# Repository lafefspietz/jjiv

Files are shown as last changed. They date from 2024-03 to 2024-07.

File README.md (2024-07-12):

# [JJIV](https://github.com/lafefspietz/jjiv/)

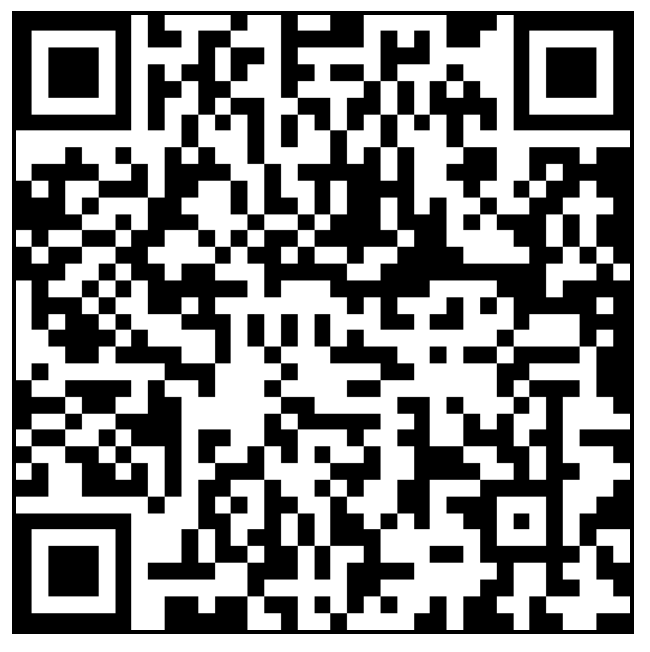
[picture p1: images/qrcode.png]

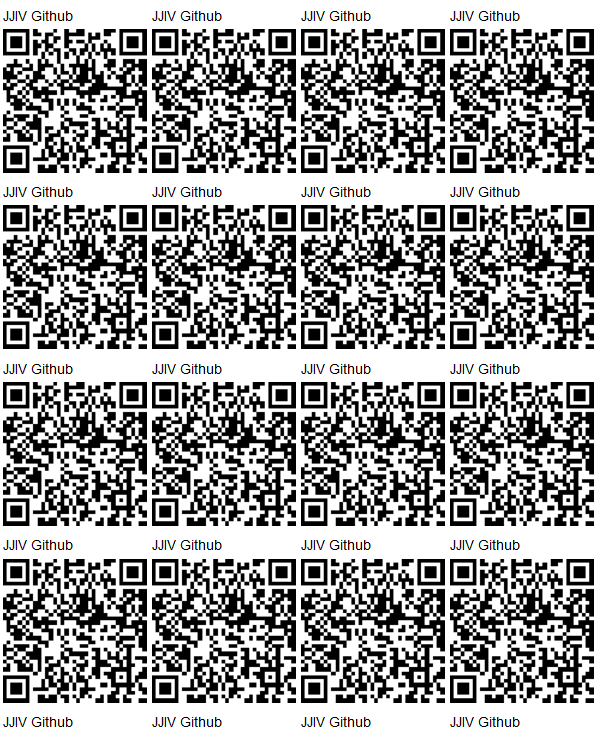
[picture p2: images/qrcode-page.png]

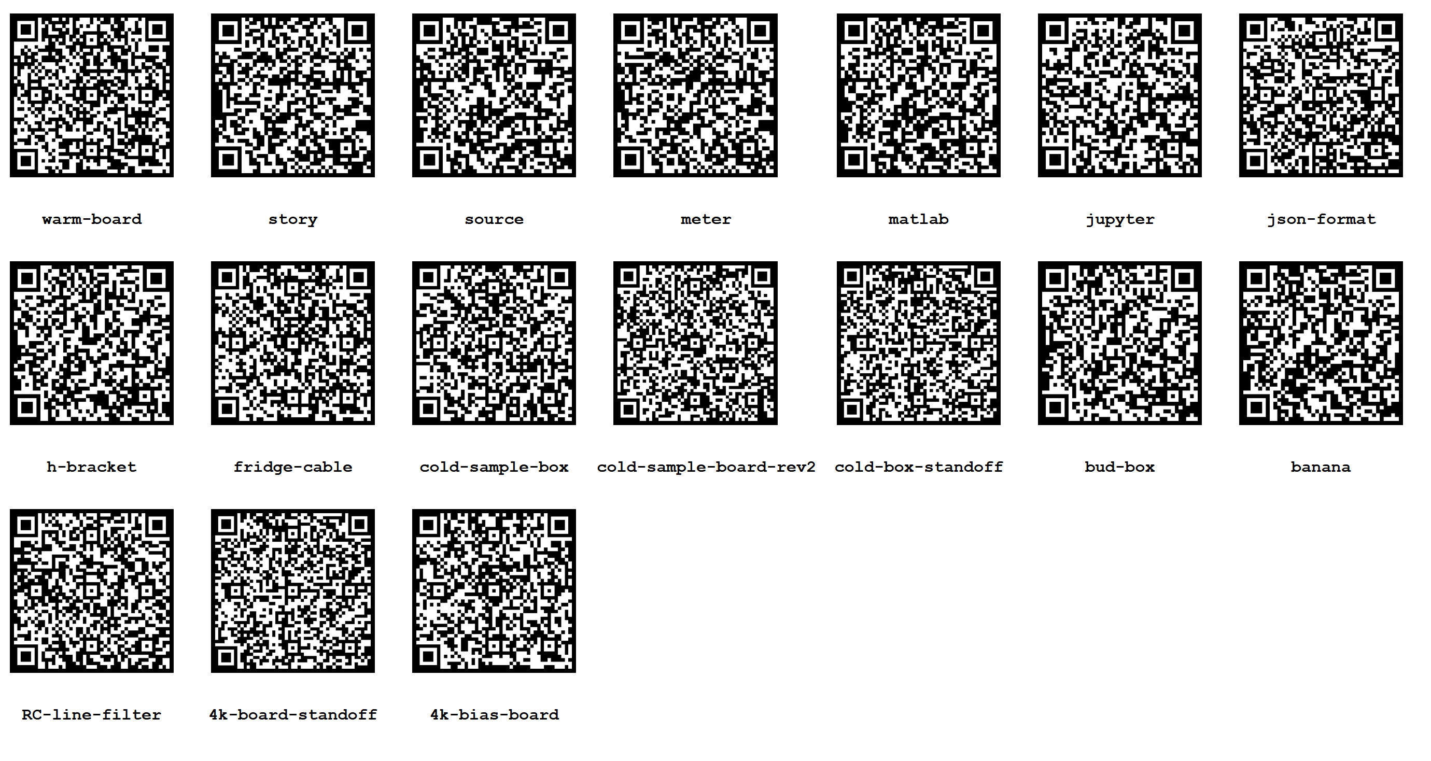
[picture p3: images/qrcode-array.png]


 - [readme reader](readme/readme-reader.html)
 - [readme editor](readme/readme-editor.html)


# JJIV: Josephson Junction IV Curve Tracer System

[Open source hardware instrument](https://github.com/lafelabs/OSHI) for measuring the current-voltage characteristics(IV curves) of [Josephson Junctions](https://en.wikipedia.org/wiki/Josephson_effect) via a true symmetric twisted pair measurement.  

The story behind this system can be read in the [story Readme here](story/README.md).

## Mechanical elements

 - [Bud Box and Rack Mount](bud-box/)
 - [H Bracket](h-bracket/)
 - [4k Board Standoff](4k-board-standoff/)
 - [Sample Enclosure Standoff](cold-box-standoff/)
 - [Sample Enclosure](cold-sample-box/)

## Electrical Elements

 - One [Yokogawa GS200 DC Voltage / Current Source](source/)
 - Two [Volt Meters](meter/)
 - [Banana Cables](banana/)
 - [Warm Board](warm-board/)
 - [DB25 to Fischer Fridge Cable](fridge-cable/)
 - [4k Bias Board](4k-bias-board/)
 - [Sample Board](cold-sample-board-rev2/)
 
## Software Elements

 - [Matlab IV Curves](matlab/)
 - [Data Format](json/)

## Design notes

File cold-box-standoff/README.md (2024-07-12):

## [Back to JJIV](../)

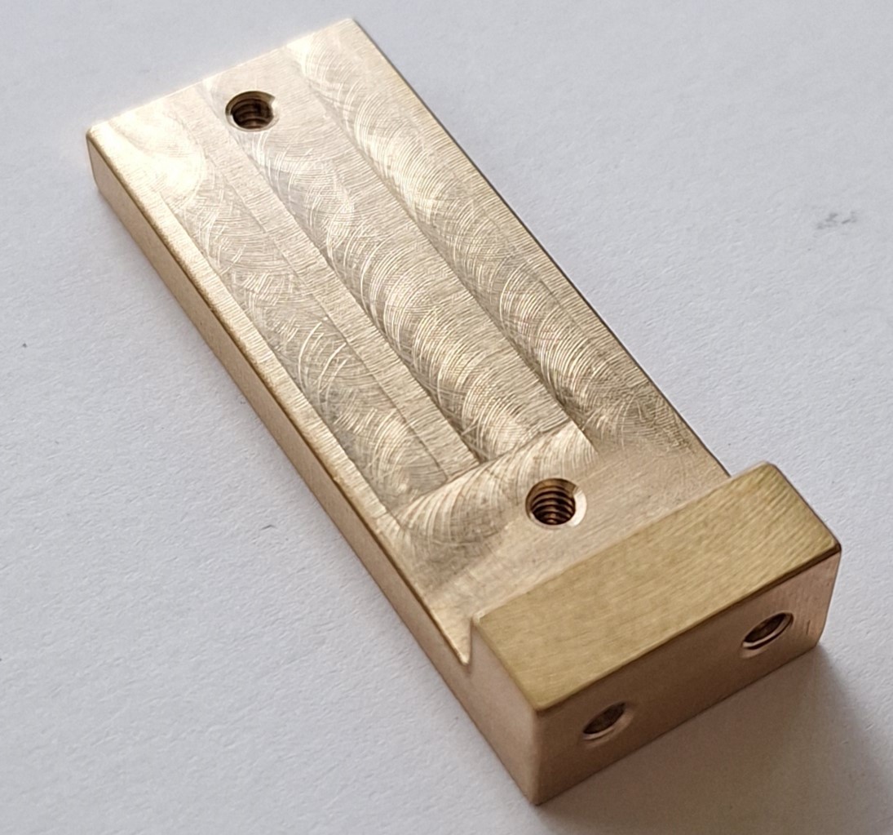
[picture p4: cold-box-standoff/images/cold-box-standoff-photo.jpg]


# Cold Box Standoff

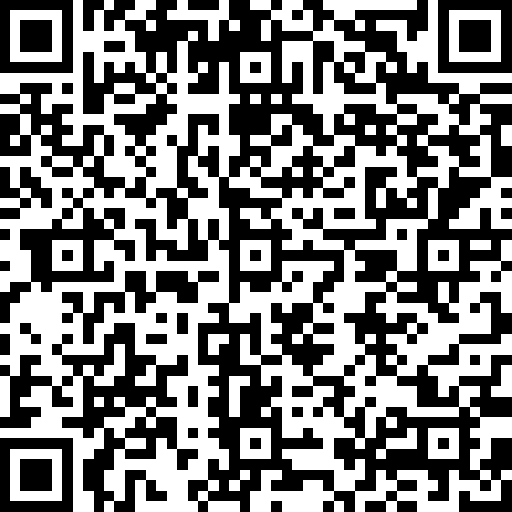
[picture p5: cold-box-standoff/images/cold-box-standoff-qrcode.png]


This brass machined part connects the [H Bracket](../h-bracket/) in the JJIV system with the [cold sample box](../cold-sample-box/) by way of two lenghts of 4-40 brass screws.  In order to order this you will need the .pdf and .step files below.  We had prototypes machined by [pcbway.com](https://pcbway.com) in the spring of 2024.  

These will be made available on artists' web pages so people can buy small numbers of them.

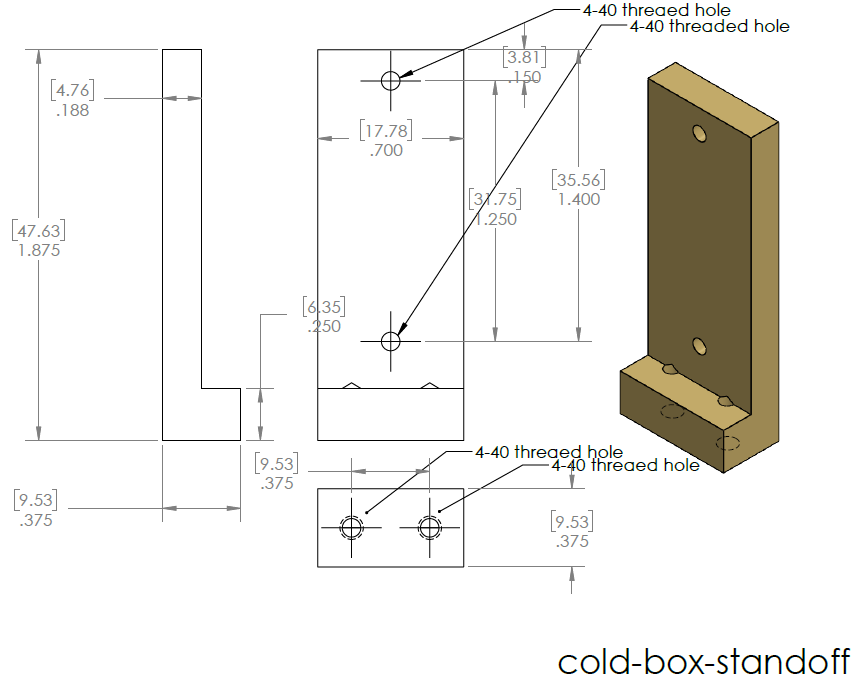
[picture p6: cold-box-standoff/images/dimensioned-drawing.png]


 - [cold-box-standoff.SLDDRW](cold-box-standoff.SLDDRW)
 - [cold-box-standoff.SLDPRT](cold-box-standoff.SLDPRT)
 - [cold-box-standoff.pdf](cold-box-standoff.pdf)
 - [cold-box-standoff.STEP](cold-box-standoff.STEP)
 - [cold-box-standoff.STL](cold-box-standoff.STL)
 
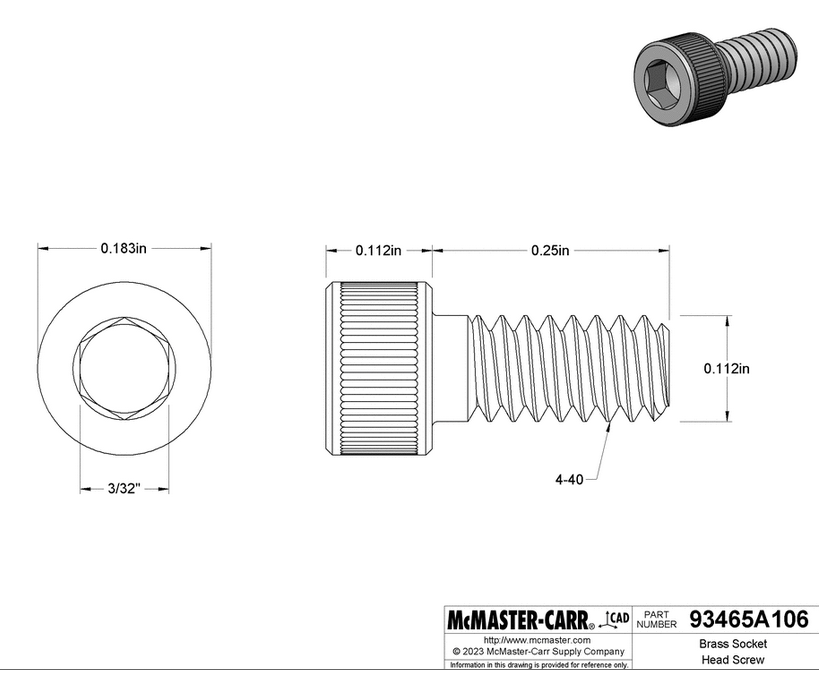
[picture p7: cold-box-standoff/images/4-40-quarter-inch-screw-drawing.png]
(https://www.mcmaster.com/93465A106/)


[Ball-End Hex L-Key, McMaster-Carr part number 57185A11](https://www.mcmaster.com/57185A11/)

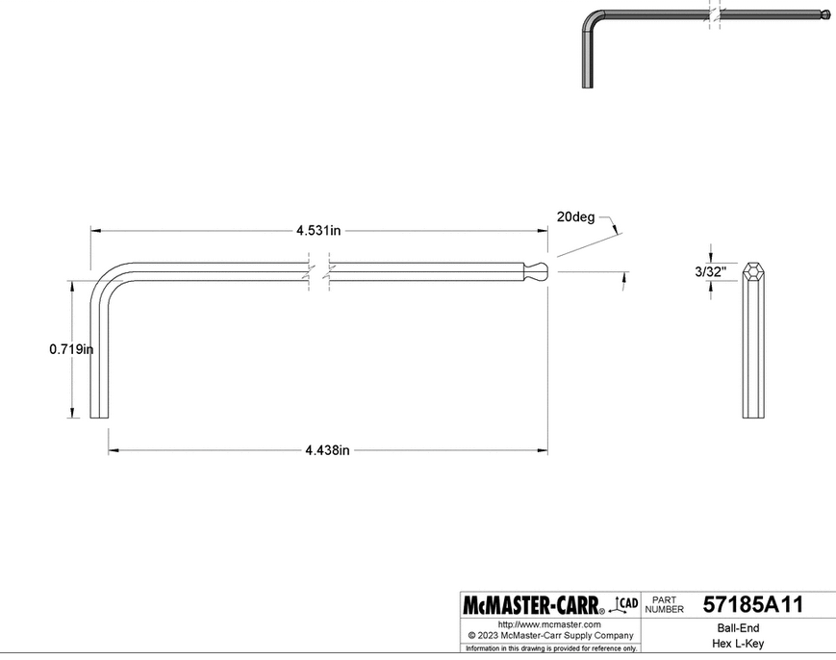
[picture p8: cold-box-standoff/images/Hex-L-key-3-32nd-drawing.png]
(https://www.mcmaster.com/57185A11/)


## T Standoff

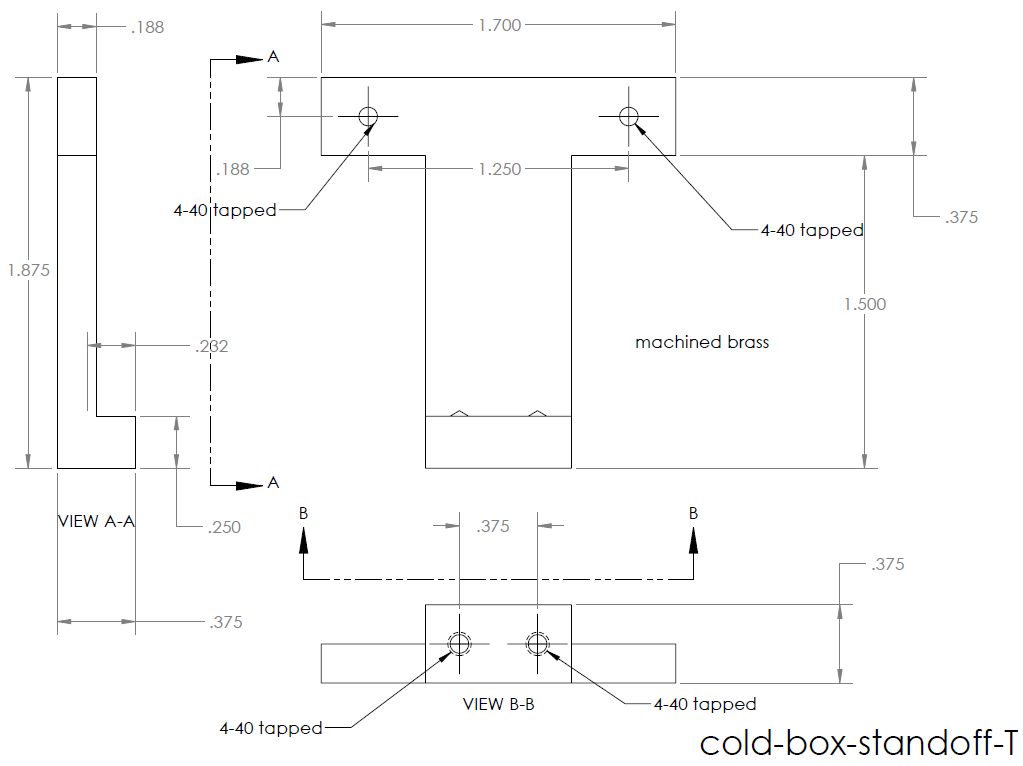
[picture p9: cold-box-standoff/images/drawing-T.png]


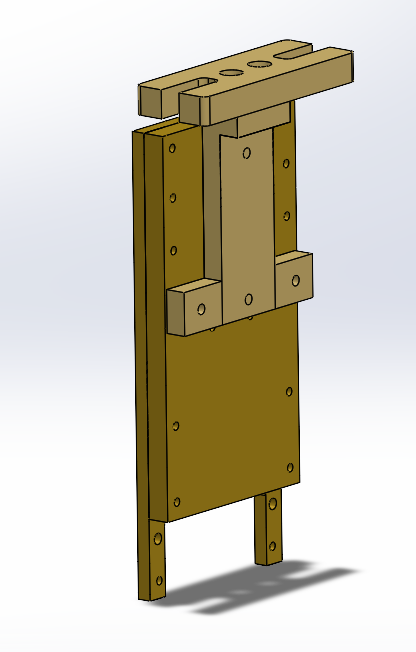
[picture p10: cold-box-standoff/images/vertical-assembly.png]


 - [cold-box-standoff-T.SLDDRW](cold-box-standoff-T.SLDDRW)
 - [cold-box-standoff-T.SLDPRT](cold-box-standoff-T.SLDPRT)
 - [cold-box-standoff-T.STEP](cold-box-standoff-T.STEP)
 - [cold-box-standoff-T.pdf](cold-box-standoff-T.pdf)

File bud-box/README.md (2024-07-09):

## [Back to Main JJIV](../)

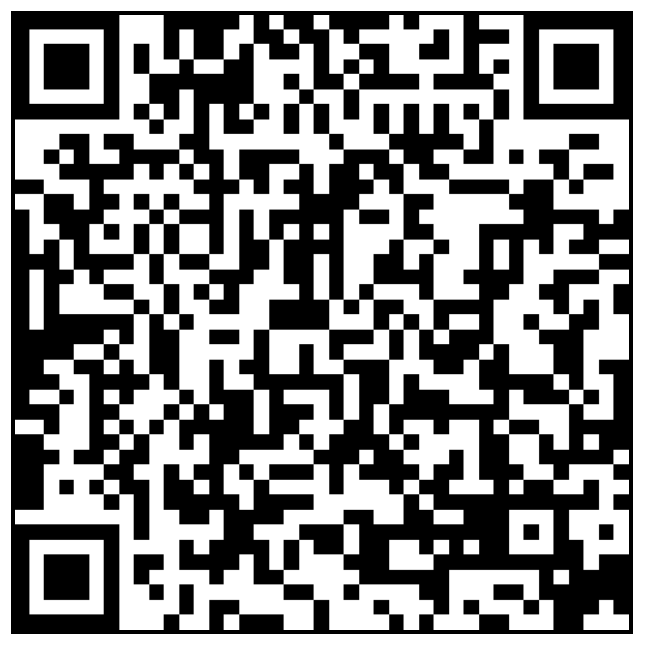
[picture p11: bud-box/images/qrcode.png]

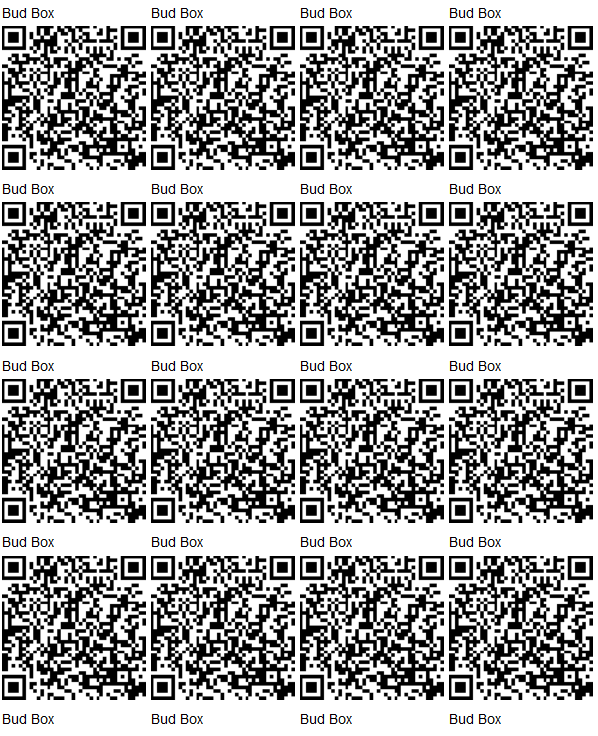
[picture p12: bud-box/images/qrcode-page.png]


# [Bud Box](https://github.com/lafefspietz/jjiv/tree/main/bud-box)

 - [warm Board](../warm-board/)
 - [CU-347 Bud Box from Hawkusa](https://www.hawkusa.com/manufacturers/bud/enclosures/cu-347)
 - [Rack Mount DIN rail from Amazon](https://www.amazon.com/WatchfulEyE-Mounting-Bracket-Aluminum-Oxidation/dp/B08F4WQX1Z)
 - [Din rail clips](https://www.digikey.com/en/products/detail/phoenix-contact/1201578/290934)
 - [Din rail clip screws](https://www.amazon.com/uxcell-100pcs-Stainless-Tapping-Screws/dp/B01M0P3EUK)
 - [2 4/40 standoffs](https://www.mcmaster.com/91075A462/)
 - [1 Isolated BNC feedthrough](https://www.digikey.com/en/products/detail/amphenol-rf/112431/1011725)
 - [1 25 pin DSUB board mount/panel connector](https://www.digikey.com/en/products/detail/assmann-wsw-components/A-DF-25-PP-Z/1241794)
 - [18 5 volt relay from digikey](https://www.digikey.com/en/products/detail/comus-international/3570-1331-053/7497099)
 - [4 position Selector Switch](https://www.digikey.com/en/products/detail/c-k/A10405RNZQ/3751696) 
 - [6 Banana Jacks](https://www.digikey.com/en/products/detail/cinch-connectivity-solutions-johnson/108-0907-001/5932)
 - [6 Banana plug wires](https://www.digikey.com/en/products/detail/pomona-electronics/B-12-4/737916)
 - [3d printed switch knob](knob.stl)
 - [Color coded solid hookup wire](https://www.digikey.com/en/products/detail/adafruit-industries-llc/1311/6198255)

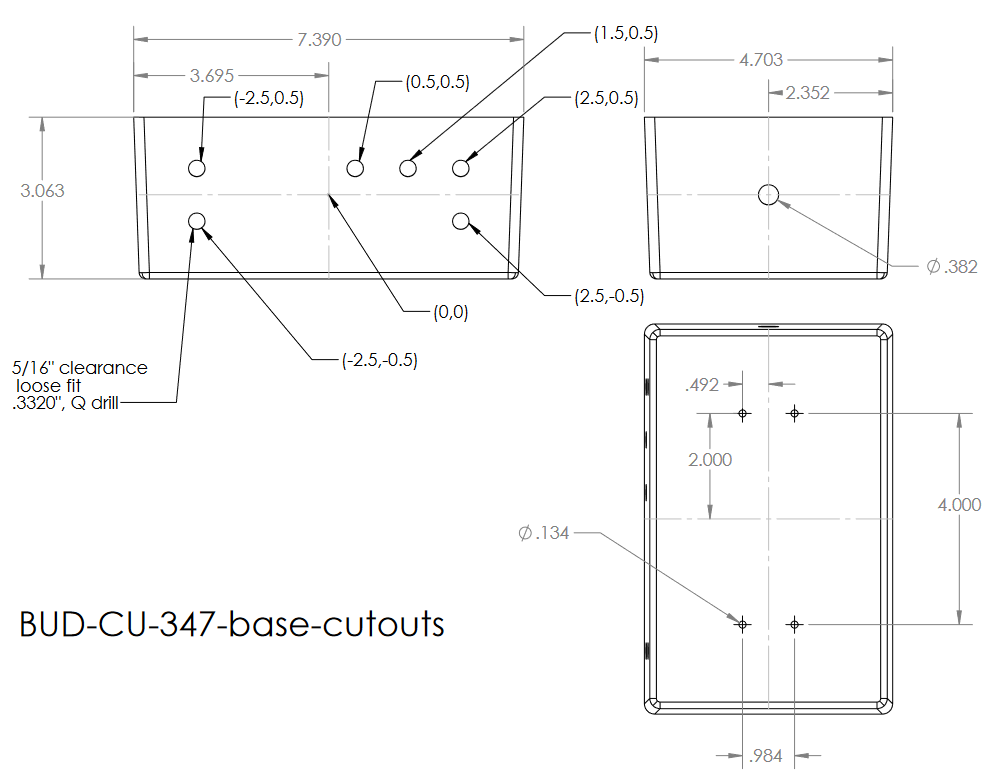
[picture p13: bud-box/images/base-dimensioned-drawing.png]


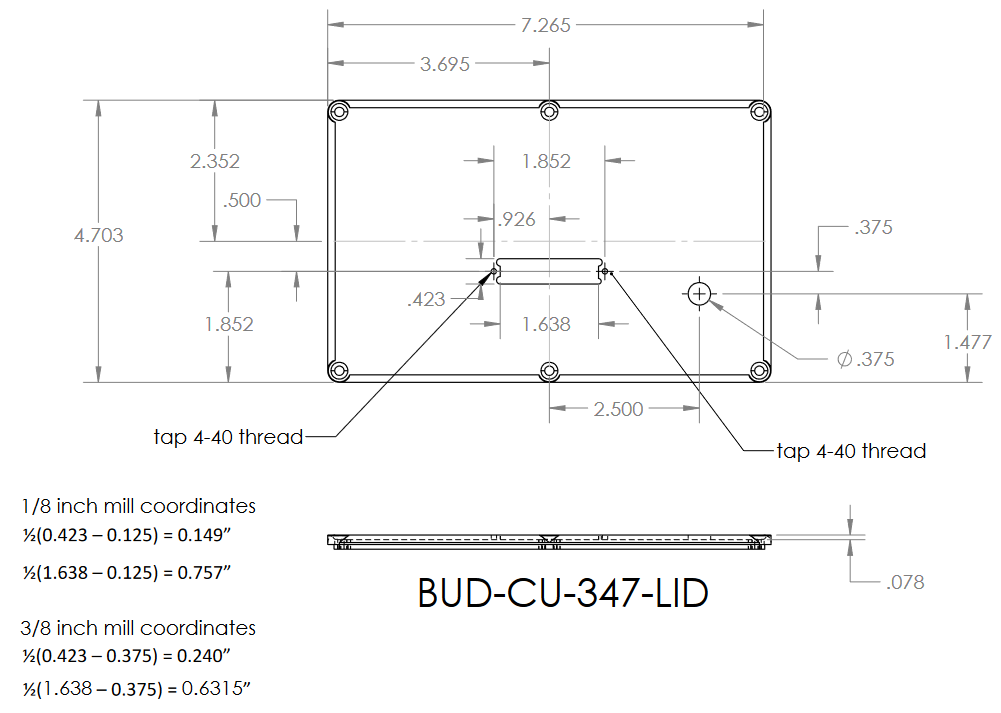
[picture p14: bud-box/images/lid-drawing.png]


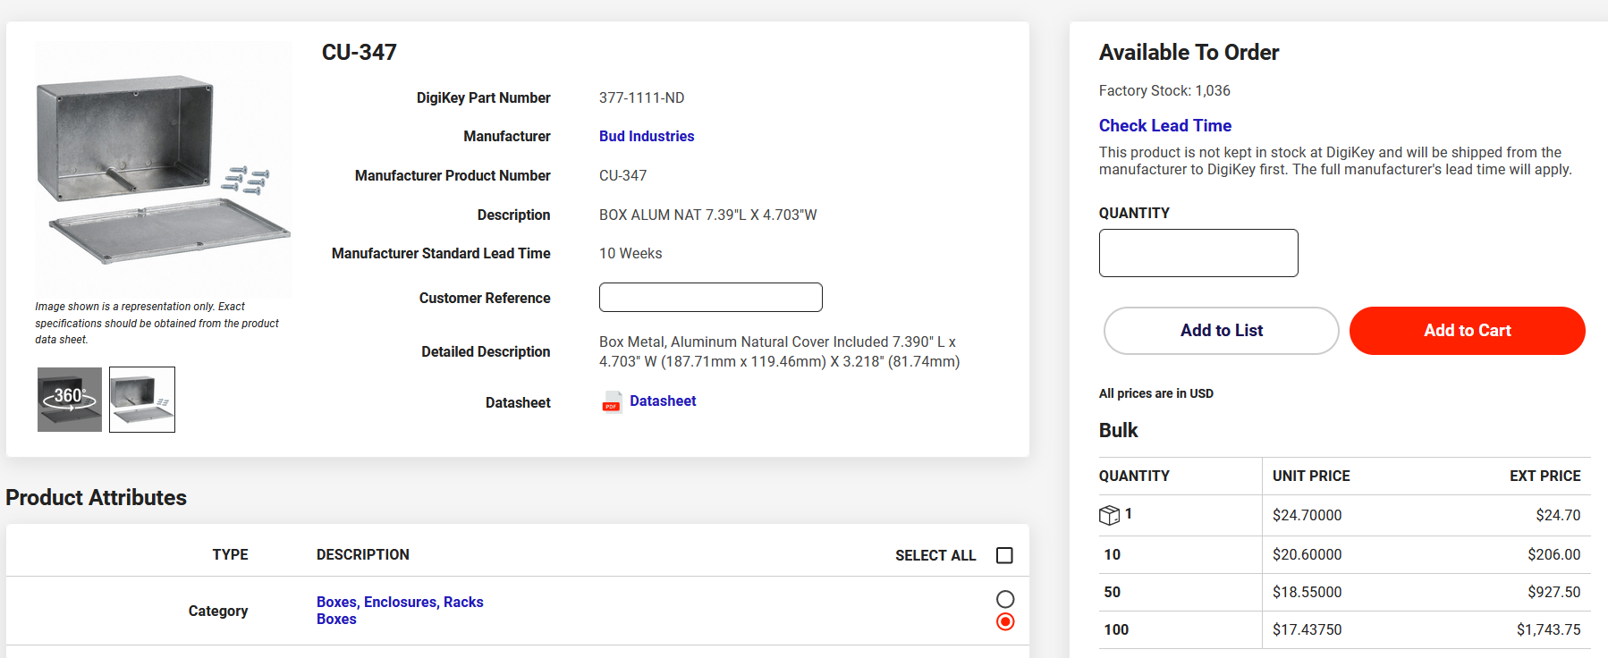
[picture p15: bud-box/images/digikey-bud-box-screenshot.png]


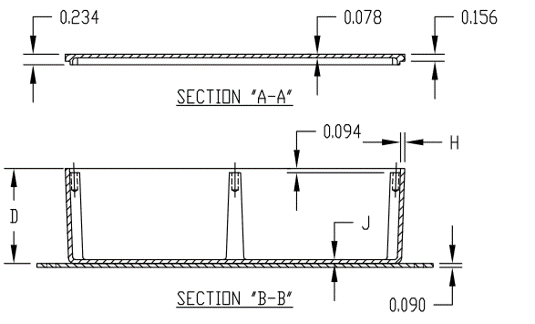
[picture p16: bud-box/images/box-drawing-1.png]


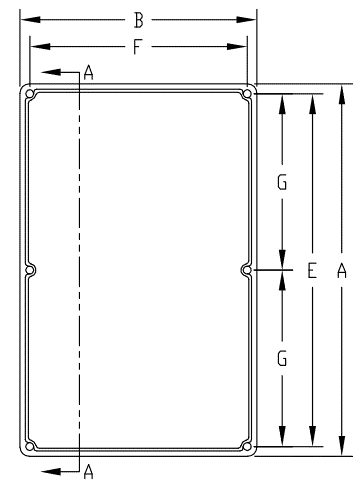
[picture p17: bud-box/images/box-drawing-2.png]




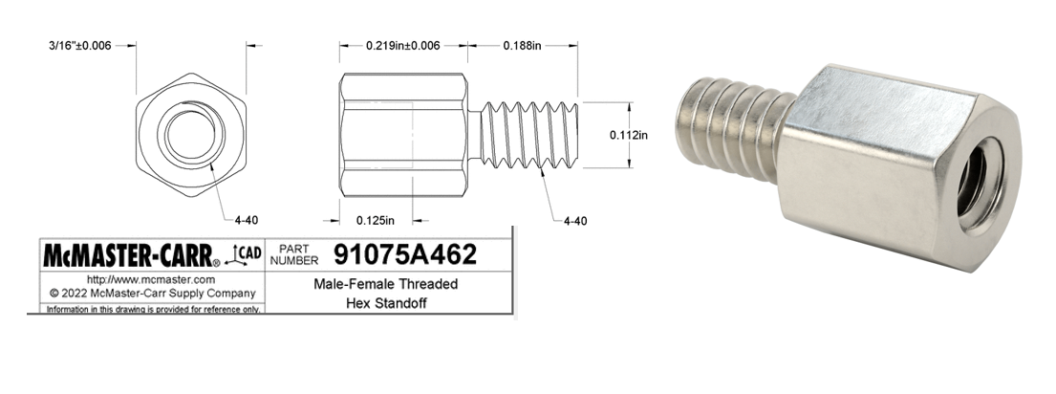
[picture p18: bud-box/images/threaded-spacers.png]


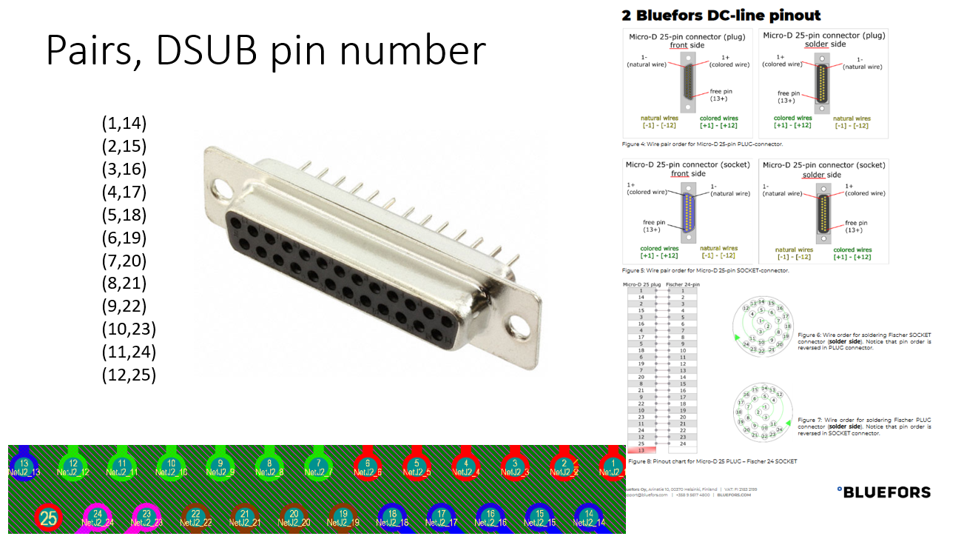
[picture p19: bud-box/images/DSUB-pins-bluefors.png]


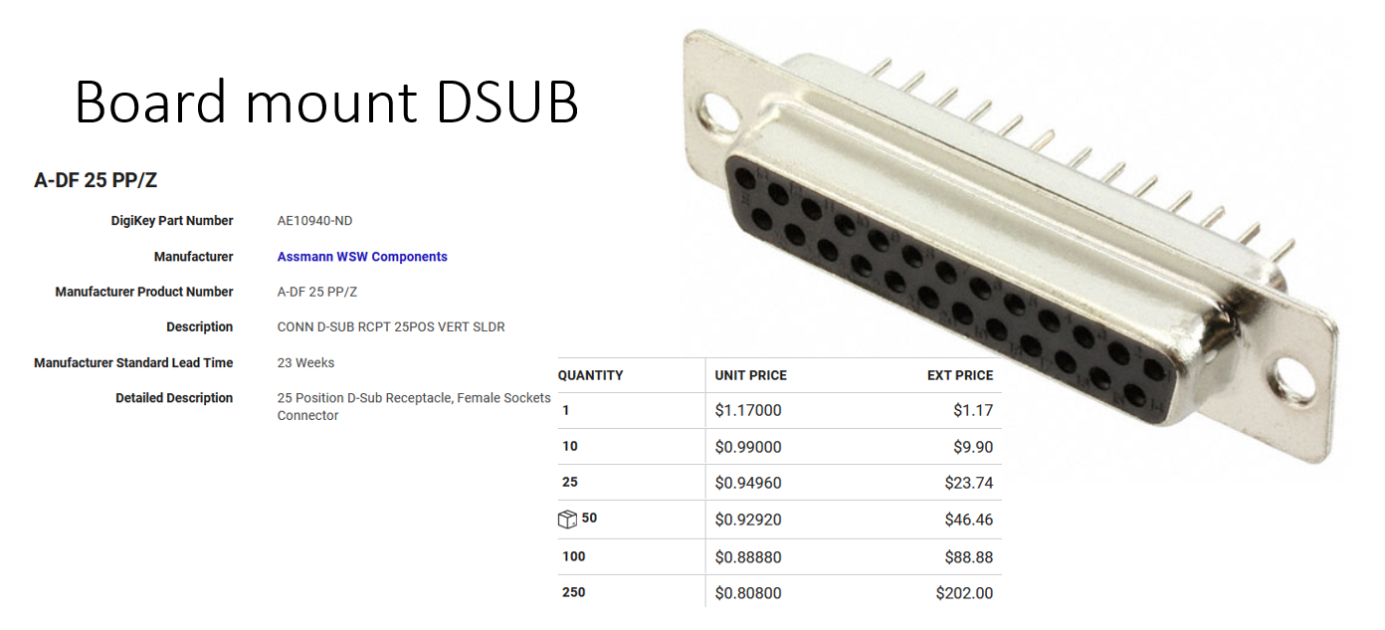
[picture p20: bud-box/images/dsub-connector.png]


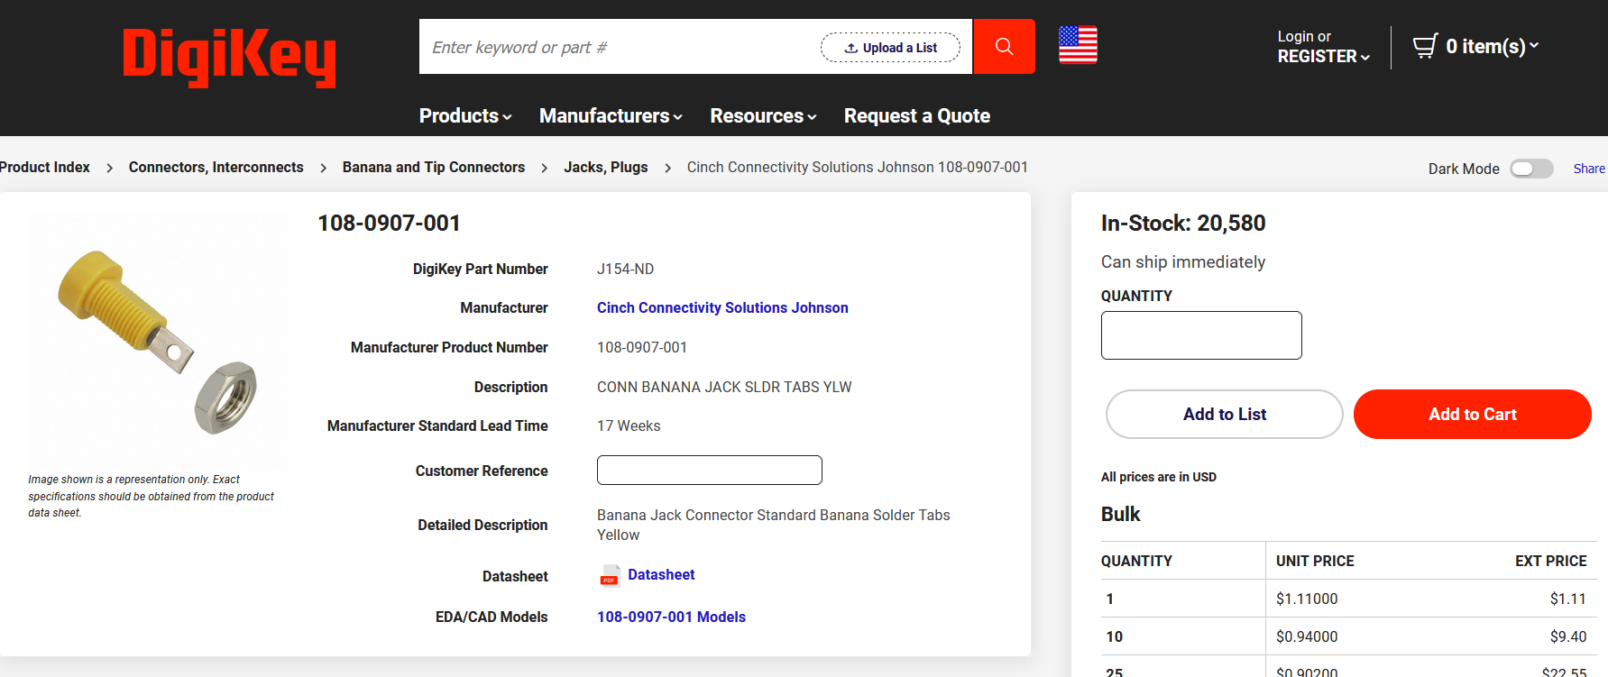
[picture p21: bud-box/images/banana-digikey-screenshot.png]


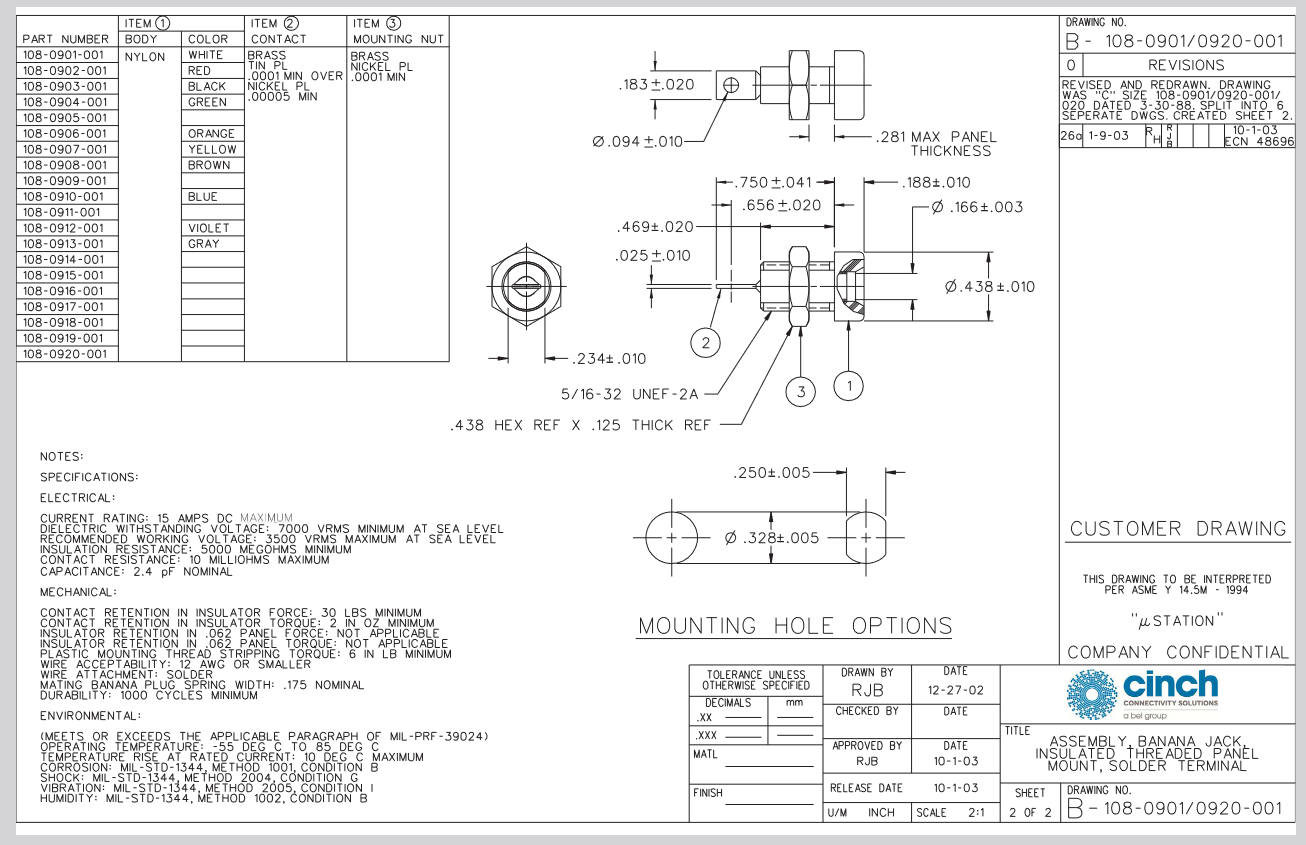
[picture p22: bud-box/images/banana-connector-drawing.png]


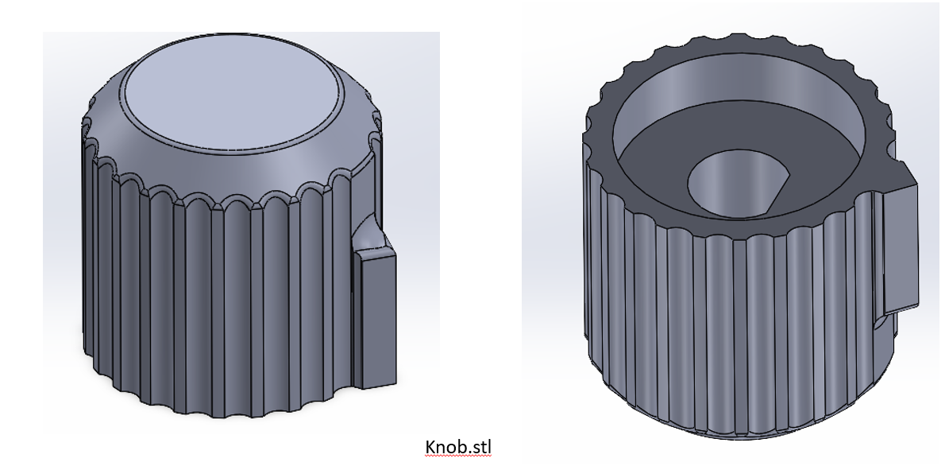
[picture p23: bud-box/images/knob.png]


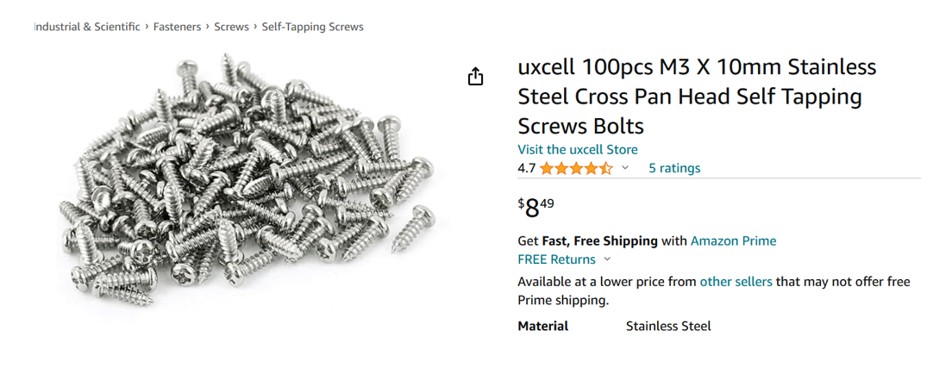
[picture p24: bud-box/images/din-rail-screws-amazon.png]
(https://www.amazon.com/WatchfulEyE-Mounting-Bracket-Aluminum-Oxidation/dp/B08F4WQX1Z)


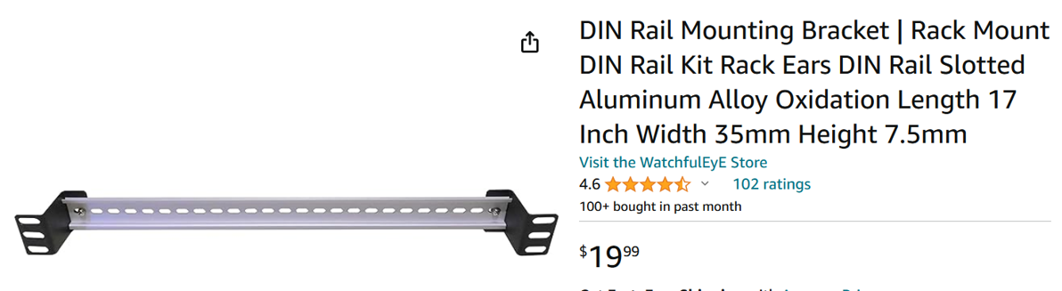
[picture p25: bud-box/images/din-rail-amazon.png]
(https://www.amazon.com/uxcell-100pcs-Stainless-Tapping-Screws/dp/B01M0P3EUK)


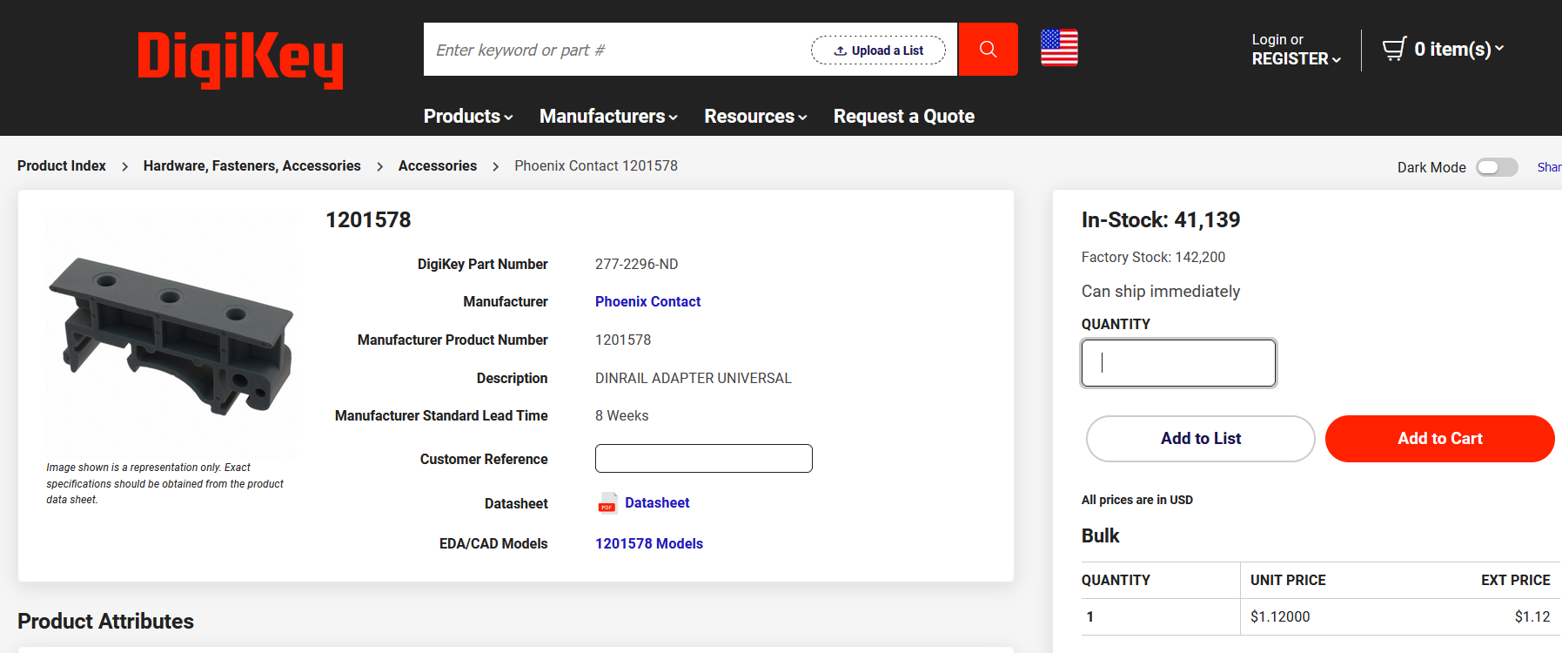
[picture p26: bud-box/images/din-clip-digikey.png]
(https://www.digikey.com/en/products/detail/phoenix-contact/1201578/290934)


## Files

 - [BUD-CU-347-LID.pdf](AN-1304-A-lid-machined.pdf)
 - [BUD-CU-347-LID.SLDPRT](AN-1304-A-machined-box.SLDPRT)
 - [BUD-CU-347-LID.SLDDRW](BUD-CU-347-LID.SLDDRW)
 - [BUD-CU-347-base-cutouts.pdf](BUD-CU-347-base-cutouts.pdf)
 - [BUD-CU-347-base-cutouts.SLDDRW](BUD-CU-347-base-cutouts.SLDDRW)
 - [BUD-CU-347-base-cutouts.SLDPRT](BUD-CU-347-base-cutouts.SLDPRT)
 - [BUD-CU-347-base-cutouts.STEP](BUD-CU-347-base-cutouts.STEP)

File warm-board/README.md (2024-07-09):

## [Back to JJIV](../)

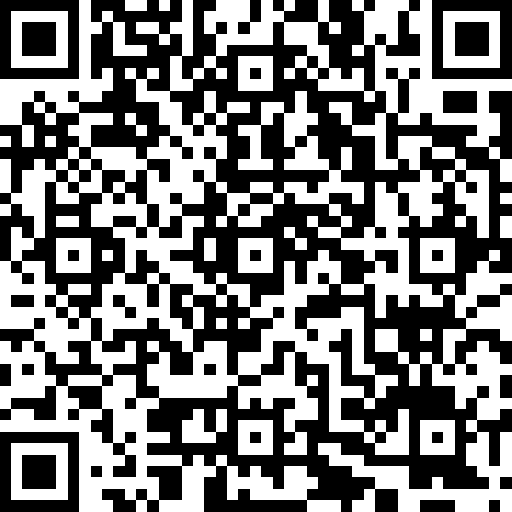
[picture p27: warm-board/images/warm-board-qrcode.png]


# Warm Board



Warm Board is the board that goes inside the [Bud Box](../bud-box) which connects the DB25 connector which goes to the dilution refrigerator with the drive, current leads and voltage leads by way of a network of electromechanical relays.  

## Files

 - [warm-pcb-gerbers.zip](warm-pcb-gerbers.zip)
 - [warm-pcb.step](warm-pcb.step)
 - [warm-board.PrjPcb](warm-board.PrjPcb)
 - [warm-board.SchDoc](warm-board.SchDoc)
 
## Bill of Materials(BOM)

 - [1x DB 25 through hole Board connector](https://www.digikey.com/en/products/detail/assmann-wsw-components/A-DF-25-PP-Z/1241794)
 - [2x 4-40 Standoffs](https://www.mcmaster.com/91075A462/)
 - [18x Relay](https://www.digikey.com/en/products/detail/comus-international/3570-1331-053/7497099)
 - [1x 4 Way Switch](https://www.digikey.com/en/products/detail/c-k/A10405RNZQ/3751696)
 - [Color coded solid hookup wire](https://www.digikey.com/en/products/detail/adafruit-industries-llc/1311/6198255)
 - [6x Banana Jacks](https://www.digikey.com/en/products/detail/cinch-connectivity-solutions-johnson/108-0907-001/5932)
 - [Isolated BNC Feedthrough for power]( https://www.digikey.com/en/products/detail/amphenol-rf/112431/1011725)

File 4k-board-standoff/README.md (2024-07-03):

## [Back to Main JJIV](../)




# [4 kelvin board standoff](https://github.com/lafefspietz/jjiv/tree/main/4k-board-standoff)

This is the machined brass standoff which connects the [H Bracket](../h-bracket/) with the [../4k-bias-board/].  It has 4-40 threaded holes which are used for both of these connections.  To order these from a machine shop you will need the .pdf and .step files below.  



## Files

 - [4k-board-standoff.SLDPRT](4k-board-standoff.SLDPRT)
 - [4k-board-standoff.SLDDRW](4k-board-standoff.SLDDRW)
 - [4k-board-standoff.pdf](4k-board-standoff.pdf)
 - [4k-board-standoff.STEP](HBracket-M4.STEP)
 - [4k-board-standoff.STL](4k-board-standoff.STL)
 - [1/4 inch 4-40 Brass Screw model](93465A106_Brass-Socket-Head-Screw.SLDPRT)







[Quarter inch 4-40 brass socket head screw, McMaster-Carr part number 93465A106](https://www.mcmaster.com/93465A106/)

(https://www.mcmaster.com/93465A106/)

[Ball-End Hex L-Key, McMaster-Carr part number 57185A11](https://www.mcmaster.com/57185A11/)

(https://www.mcmaster.com/57185A11/)

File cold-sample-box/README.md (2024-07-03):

## [Back to JJIV](../)



# Cold Sample Box

This metal box closes directly over the bare copper on the circuit board, and the soldermask covering the lines going into the sample space.  There is about 1 mm vertical distance in the cavity where the samples are placed.  RF absorbent foam can be used over the RC line filters in the [cold sample board](../cold-sample-board-rev2/) to further block very high frequency signals. 

This enclosure aims to be a very cold and dark space with effective heat sinking to the base of a dilution refrigerator.  The two parts are held together with 2-56 screws, and are attached to the [cold box standoff](../cold-box-standoff/) by 4-40 screws.  

We had the prototypes built out of brass by [PCBWay.com](https://pcbway.com) in the spring of 2024, and are testing them now over the summer of 2024.  To order them from any machine shop, you will need the .pdf and the .step files below.  You need to get both a top and a bottom for each JJIV kit.  Also listed below are the screws you need to assemble everything and the hex wrenches for those screws. It's always a good idea to add those hex wrenches to your parts order so you don't have to hunt for those sizes during assembly.

These can be bought and sold by artists on the Internet as well, to take advantage of economies of scale from the machine shop.





 - [cold-sample-box-bottom.pdf](cold-sample-box-bottom.pdf)
 - [cold-sample-box-bottom.STEP](cold-sample-box-bottom.STEP)
 - [cold-sample-box-bottom.SLDPRT](cold-sample-box-bottom.SLDPRT)
 - [cold-sample-box-bottom.SLDDRW](cold-sample-box-bottom.SLDDRW)
 


 - [cold-sample-box-top.pdf](cold-sample-box-top.pdf)
 - [cold-sample-box-top.SLDDRW](cold-sample-box-top.SLDDRW)
 - [cold-sample-box-top.SLDPRT](cold-sample-box-top.SLDPRT)
 - [cold-sample-box-top.STEP](cold-sample-box-top.STEP)
 
## Fasteners

 - [2-56 brass socket cap screws 5/16" length McMAster Part number 93465A078](https://www.mcmaster.com/93465A078/)
 - [4-40 brass socket cap screws 3/8" length McMaster part number 93465A108](https://www.mcmaster.com/93465A108/)
 - [5/64 Allan Wrench](https://www.mcmaster.com/57185A43/)
 - [3/32 Allan Wrench](https://www.mcmaster.com/57185A11/)

(https://www.mcmaster.com/93465A078/)

(https://www.mcmaster.com/93465A108/)

(https://www.mcmaster.com/57185A11/)

(https://www.mcmaster.com/57185A43/)

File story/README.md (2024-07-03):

## [Back to JJIV](../)

# JJIV Story



[Josephson Junctions](https://en.wikipedia.org/wiki/Josephson_effect) are electronic devices consisting of two superconducting electrodes separated by an insulating barrier thin enough to allow for [quantum tunneling](https://en.wikipedia.org/wiki/Quantum_tunnelling).  They are analog devices that have been used for [voltage standards](https://en.wikipedia.org/wiki/Josephson_voltage_standard), mixers, detectors, synthesizers, and as the main element to the [superconducting approaches](https://en.wikipedia.org/wiki/Superconducting_quantum_computing) to [quantum computer](https://en.wikipedia.org/wiki/Quantum_computing) development.

This is a system for measuring current-voltage(IV) curves of low critical current(10's of nanoamps) Josephson junctions in a dilution refrigerator.  This work is being carried out in the Superconductive electronics group in the Radio Frequency Division of the Communications Technology Laboratory at the National Institute of Standards and Technology, in Boulder, Colorado.  

The initial system is built for use on a Bluefors dilution refrigerator using the built in twisted pair wiring that ships with those instruments.  

The system consists of a programmable voltage source, a pair of volt meters, a room temperature box which switches the signals between different samples, a connecting that box to the dilution fridge, a bias board with a cold voltage divider and bias resistors, and a cold sample assembly with built in filtering.      

This documentation is intended to allow other researchers to replicate the entire set of components to make a turnkey system for taking IV curves of low critical current Josephson Junctions at dilution refrigerator temperatures.  



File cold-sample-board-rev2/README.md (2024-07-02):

## [Back to JJIV](../)





# Cold Sample Board rev 2 

 - [cold-sample-board-rev2.PcbDoc](cold-sample-board-rev2.PcbDoc)
 - [cold-sample-board-rev2.pdf](cold-sample-board-rev2.pdf)
 - [cold-sample-board-rev2.PrjPcb](cold-sample-board-rev2.PrjPcb)
 - [cold-sample-board-rev2.SchDoc](cold-sample-board-rev2.SchDoc) 
 - [cold-sample-board-rev2.step](cold-sample-board-rev2.step) 
 - [cold-sample-board-rev2-bom.xlsx](cold-sample-board-rev2-bom.xlsx) 
 - [cold-sample-board-rev2-gerbers.zip](cold-sample-board-rev2-gerbers.zip) 
 - [cold-sample-board-rev2-gerbers.zip](cold-sample-board-rev2-gerbers.zip) 
 - [Pick Place for cold-sample-board-rev2.txt](Pick-Place-for-cold-sample-board-rev2.txt)

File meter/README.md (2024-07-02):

## [Back to JJIV](../)



# Meter



We need two of these to take IV curves, one for the voltage and one for the current. They are controlled via GPIB in [Matlab](../matlab).

 - [keysight link](https://www.keysight.com/us/en/product/34401A/digital-multimeter-6-digit.html)
 - [Used from bellnw for $895](https://www.bellnw.com/products/keysight-34401a)
 - [Used from valuetronics for $795](https://www.valuetronics.com/product/34401a-agilent-multimeter-used)

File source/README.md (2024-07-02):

## [Back to JJIV](../)



# Source

One Yokogawa GS200 voltage source drives the twisted pairs.



 - [yokogawa link](https://tmi.yokogawa.com/us/solutions/products/generators-sources/source-measure-units/gs200/)
 - [Used from transcat for $3,995](https://www.transcat.com/yokogawa-gs210-used-for-sale-dc-voltage-current-source)

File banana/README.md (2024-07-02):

## [Back to JJIV](../)





# Banana

 - [Banana jack](https://www.digikey.com/en/products/detail/cinch-connectivity-solutions-johnson/108-0907-001/5932)
 - [Banana Cable](https://www.digikey.com/en/products/detail/pomona-electronics/B-12-4/737916)
 - [Wikipedia entry](https://en.wikipedia.org/wiki/Banana_connector)

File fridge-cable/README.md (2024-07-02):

## [Return to JJIV](../)

# Fridge Cable

From DSUB to Fischer, twisted pair cable.

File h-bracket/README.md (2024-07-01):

## [Back to Main JJIV](../)





# [M4 H Bracket](https://github.com/lafefspietz/jjiv/tree/main/h-bracket)

This H Bracket is designed for a maximally flexible way to mount experiments in a dilution refrigerator. It is common in dilution refrigerators for there to be arrays of M4 threaded holes in both the mixing chamber and 4 kelvin plates. 

The H bracket can be slid around and mounted in any orientation or position in these arrays using a pair of M4 screws, which generally come with the dilution refrigerator.  

The H bracket is so named because it resembles the capital letter "H".

Several of these were ordered from PcbWay in the spring of 2024 at NIST.  In our initial design, however, we mistakenly designed the slots for M3 screws and had to modify them in the machine ship after the fact. The corrected slot size is close enough to 3/16 of an inch that it was possible to use a 3/16 inch end mill to cut out the slots with a single cut on the milling machine.

These brackets are designed to be connected to the rest of an experiment via quarter inch 4-40 socket cap screws like the [brass ones from McMaster here](https://www.mcmaster.com/57185A11/). The screws are inset into the holes so that heads disappear, allowing the bracket to sit flush against the plate in the fridge with the heads facing the plate.   

To get these made, you will need the .step file below to get a quote, and the drawing in the .pdf can also help but is often optional. 

## Files

 - [HBracket-M4.SLDPRT](HBracket-M4.SLDPRT)
 - [HBracket-M4.SLDDRW](HBracket-M4.SLDDRW)
 - [HBracket-M4.pdf](HBracket-M4.pdf)
 - [HBracket-M4.STEP](HBracket-M4.STEP)
 - [HBracket-M4.STL](HBracket-M4.STL)
 - [1/4 inch 4-40 Brass Screw model](93465A106_Brass-Socket-Head-Screw.SLDPRT)





[Quarter inch 4-40 brass socket head screw, McMaster-Carr part number 93465A106](https://www.mcmaster.com/93465A106/)

(https://www.mcmaster.com/93465A106/)

[Ball-End Hex L-Key, McMaster-Carr part number 57185A11](https://www.mcmaster.com/57185A11/)

(https://www.mcmaster.com/57185A11/)

[M4 10 mm brass screw, McMaster-Carr part number 90349A109](https://www.mcmaster.com/90349A109/)

(https://www.mcmaster.com/90349A109/)

[3mm hex L key, McMaster-Carr part number 6958A13](https://www.mcmaster.com/6958A13/)

(https://www.mcmaster.com/6958A13/)

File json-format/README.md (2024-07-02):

## [Return to JJIV](../)





# JSON Format

[JSON](https://en.wikipedia.org/wiki/JSON) is the "JavaScript Object Notation", a universal data storage format. A standard for saving files in .txt format with JSON in them to be used by all data analysis software written by the JJIV user community.

 - **D** is drive in volts
 - **I** is current in amperes
 - **V** is voltage in volts
 - **Rbias** is bias resistor  value in ohms
 - **npoints** is the number of points
 - **Dmin** and **Dmax** are mininum and maximum **D** values
 - **Rn** is calculated normal resistance in ohms
 - **Ic** is critical current in amperes
 - **temperature** is the temperature in kelvin
 - **username** is a username internal to the JJIV data network for whoever took the data
 - **timestamp** is the [UNIX timestamp](https://en.wikipedia.org/wiki/Unix_time) value when the data started being taken
 - **filename** is the file name of the JSON structure, which should end with .txt

## Example:

```
{
  "D": [
    -0.1,
    -0.098,
    -0.096,
    -0.094,
    -0.092,
    -0.090000000000000011,
    -0.088000000000000009,
    -0.086000000000000007,
    -0.084,
    -0.082,
    -0.08,
    -0.078000000000000014,
    -0.076000000000000012,
    -0.07400000000000001,
    -0.072000000000000008,
    -0.07,
    -0.068,
    -0.066,
    -0.064,
    -0.062000000000000006,
    -0.060000000000000005,
    -0.058,
    -0.056000000000000008,
    -0.054000000000000006,
    -0.052000000000000005,
    -0.05,
    -0.048,
    -0.046000000000000006,
    -0.044000000000000004,
    -0.042,
    -0.040000000000000008,
    -0.038000000000000006,
    -0.036000000000000004,
    -0.034,
    -0.032,
    -0.03,
    -0.027999999999999997,
    -0.026000000000000009,
    -0.024000000000000007,
    -0.022000000000000006,
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
  ],
  "V": [
    -0.000349672,
    -0.00033222,
    -0.000331843,
    -0.000324059,
    -0.000314642,
    -0.000308992,
    -0.00030962,
    -0.000307988,
    -0.000289782,
    -0.000290033,
    -0.000296436,
    -0.000279361,
    -0.000281119,
    -0.000258895,
    -0.000264922,
    -0.000243201,
    -0.000246591,
    -0.000236044,
    -0.000232654,
    -0.000221354,
    -0.00022713,
    -0.000224117,
    -0.000212314,
    -0.000209175,
    -0.000199508,
    -0.000191221,
    -0.00017515,
    -0.00017741,
    -0.000170002,
    -0.00015707,
    -0.000154057,
    -0.000156317,
    -0.000145142,
    -0.000146147,
    -0.000130327,
    -0.000116767,
    -0.000116264,
    -0.000104337,
    -0.00010961,
    -0.000104337,
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
  ],
  "IV": [
    -0.000286271,
    -0.000281183,
    -0.000271877,
    -0.00026865,
    -0.000254753,
    -0.000252767,
    -0.000241723,
    -0.000236636,
    -0.000237008,
    -0.000236884,
    -0.000215417,
    -0.000217402,
    -0.000209957,
    -0.000201891,
    -0.000192833,
    -0.000193701,
    -0.000192957,
    -0.000178563,
    -0.000167022,
    -0.000174468,
    -0.0001633,
    -0.000159577,
    -0.000149774,
    -0.000140095,
    -0.000134139,
    -0.000139847,
    -0.000123219,
    -0.000130292,
    -0.000113665,
    -0.000118876,
    -0.000102,
    -9.9767E-5,
    -0.000101876,
    -8.5E-5,
    -8.4256E-5,
    -7.4453E-5,
    -6.5518E-5,
    -6.4526E-5,
    -6.2292E-5,
    -5.1745E-5,
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
  ],
  "I": [
    -2.86271E-8,
    -2.81183E-8,
    -2.7187700000000002E-8,
    -2.6865E-8,
    -2.5475299999999998E-8,
    -2.52767E-8,
    -2.41723E-8,
    -2.36636E-8,
    -2.37008E-8,
    -2.3688400000000002E-8,
    -2.15417E-8,
    -2.17402E-8,
    -2.0995700000000002E-8,
    -2.01891E-8,
    -1.92833E-8,
    -1.93701E-8,
    -1.92957E-8,
    -1.7856299999999998E-8,
    -1.6702199999999997E-8,
    -1.74468E-8,
    -1.633E-8,
    -1.59577E-8,
    -1.49774E-8,
    -1.4009499999999999E-8,
    -1.34139E-8,
    -1.39847E-8,
    -1.2321899999999999E-8,
    -1.3029200000000001E-8,
    -1.13665E-8,
    -1.18876E-8,
    -1.02E-8,
    -9.9767E-9,
    -1.01876E-8,
    -8.5E-9,
    -8.4256E-9,
    -7.4453E-9,
    -6.5518000000000005E-9,
    -6.4526E-9,
    -6.2292000000000008E-9,
    -5.1745E-9,
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
  ],
  "Rbias": 10000,
  "npoints": 100,
  "Dmin": -0.1,
  "Dmax": 0.1,
  "Rn": null,
  "Ic": null,
  "temperature": 0.02,
  "username": "lafe",
  "url": "https://github.com/LafeFSpietz/JJIV/",
  "timestamp": "1719482712",
  "filename": "JJIV_lafe_1719482712.txt"
}
```

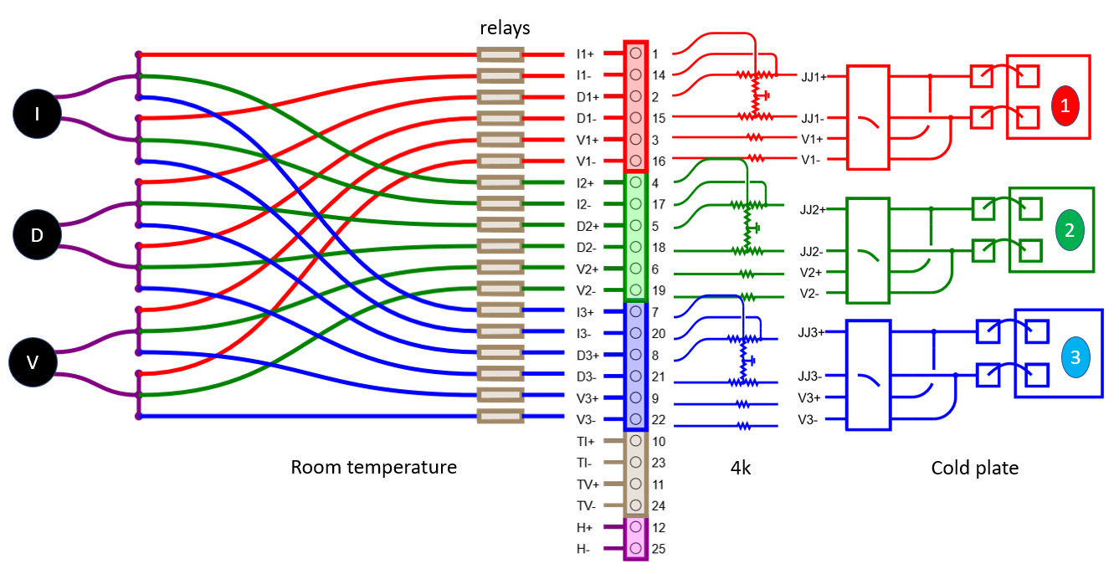
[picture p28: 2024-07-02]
images/schematic-2.png

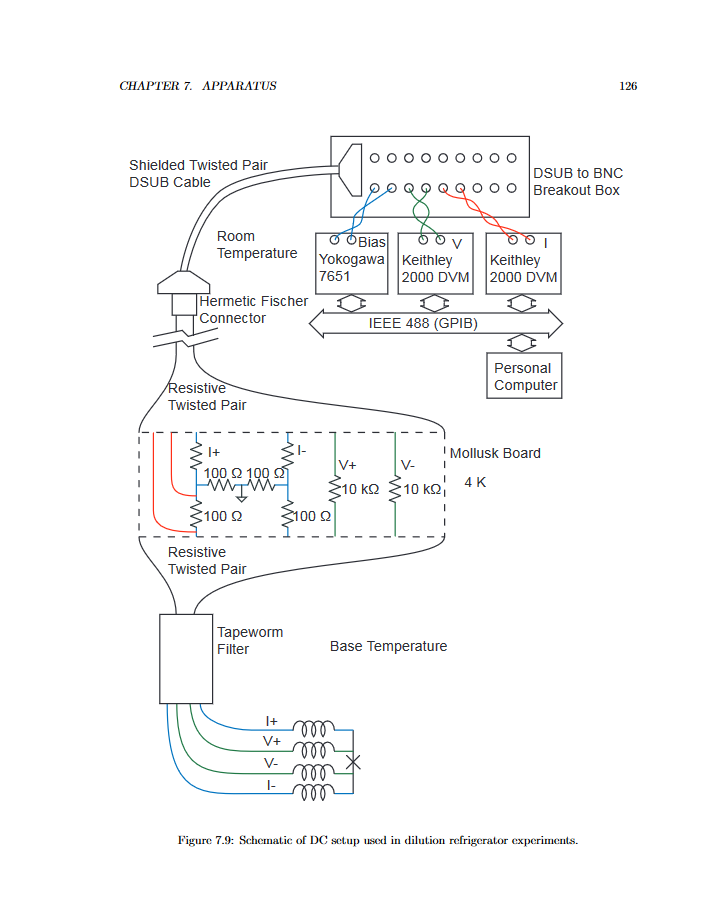
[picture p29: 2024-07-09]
images/lafe-thesis-schematic.png

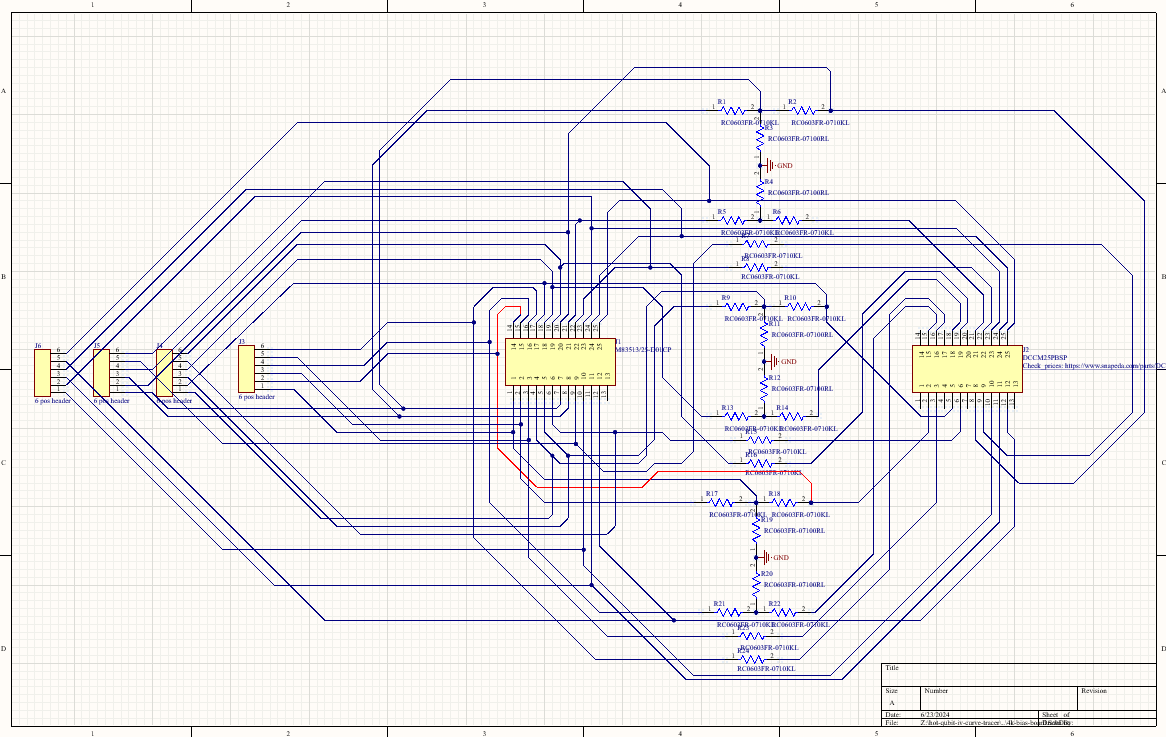
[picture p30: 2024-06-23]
4k-bias-board/images/schematic-screenshot.png

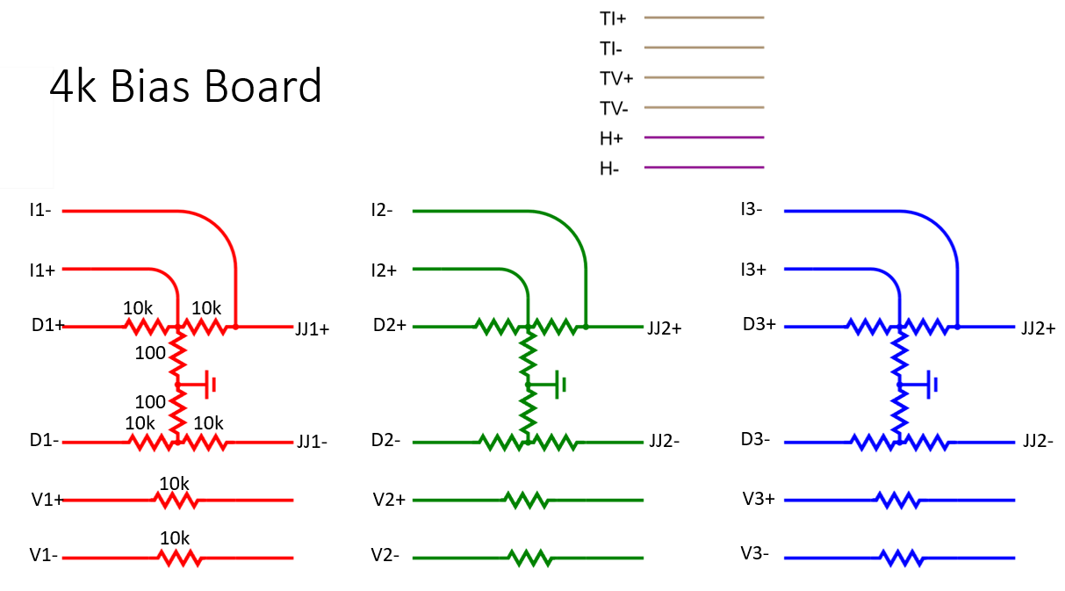
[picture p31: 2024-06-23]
4k-bias-board/images/schematic-powerpoint.png

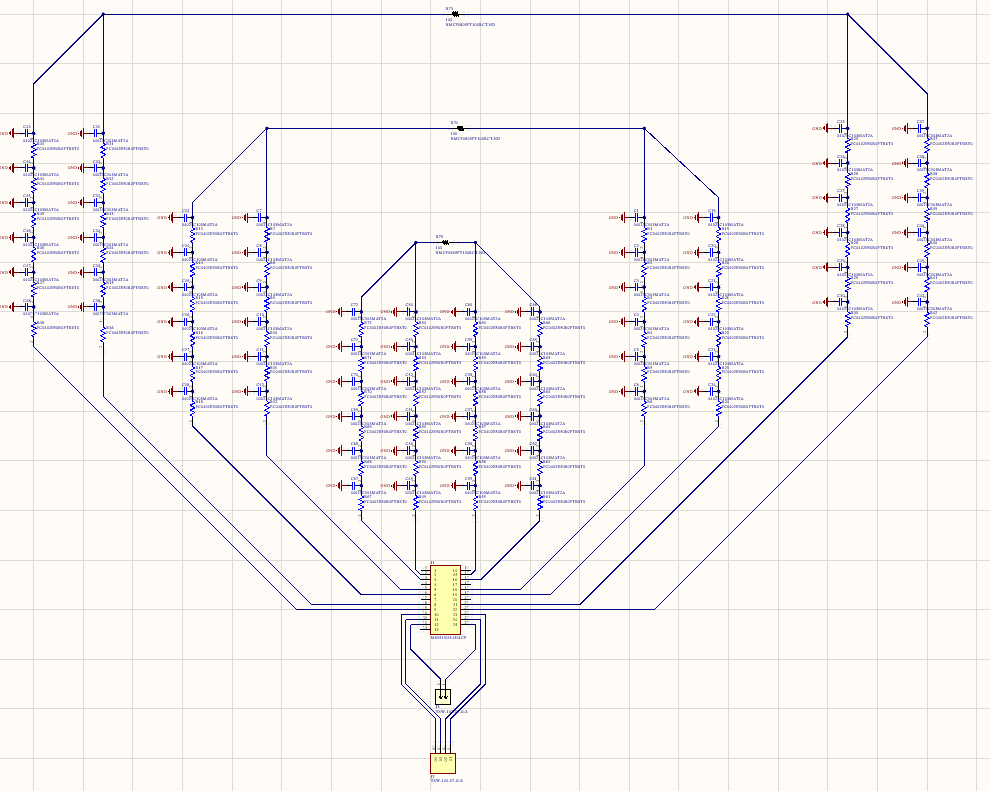
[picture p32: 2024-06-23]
cold-sample-board-rev2/images/schematic-screenshot.png

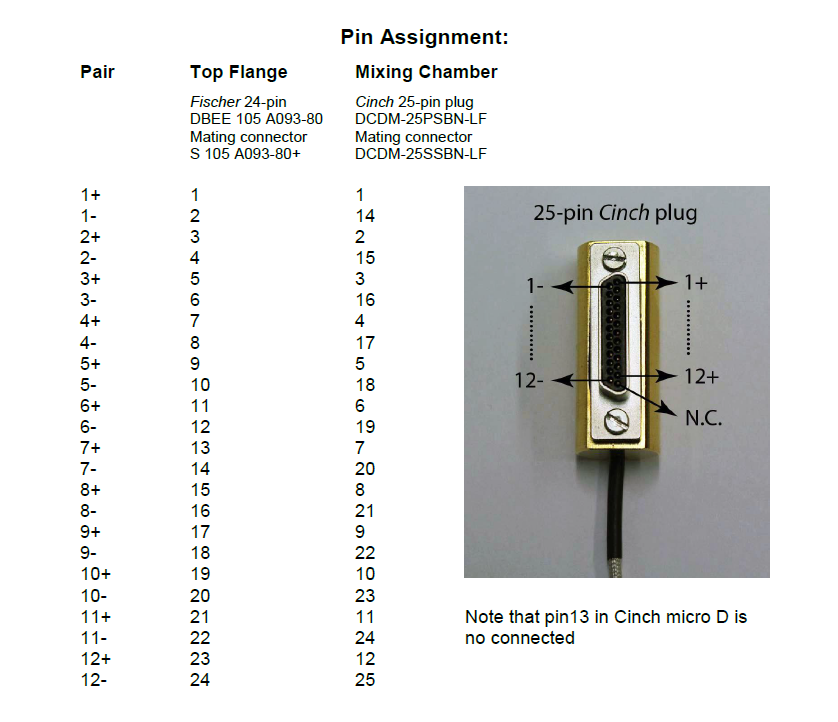
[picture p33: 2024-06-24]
images/bluefors-cold-pinout.png

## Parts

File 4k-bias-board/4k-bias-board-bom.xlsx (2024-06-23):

Description | Designator | Quantity | Manufacturer | Manufacturer Part Number
DNP | J1 | 0
DNP | J2 | 0
DNP | J3, J4, J5, J6 | 0
RES SMD 10K OHM 0.1% 1/16W 0603 | R1, R2, R5, R6, R7, R8, R9, R10, R13, R14, R15, R16, R17, R18, R21, R22, R23, R24 | 18 | TE Connectivity | CPF0603B10KE
RES SMD 100 OHM 0.1% 1/16W 0603 | R3, R4, R11, R12, R19, R20 | 6 | TE Connectivity | CPF0603B100RE

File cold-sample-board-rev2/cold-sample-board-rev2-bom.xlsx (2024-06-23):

Description | Designator | Quantity | Mfr_Name | Manufacturer_Part_Number
CAP CER 4700PF 25V X7R 0402 | C1, C2, C3, C4, C5, C6, C7, C8, C9, C10, C11, C12, C13, C14, C15, C16, C17, C18, C19, C20, C21, C22, C23, C24, C25, C26, C27, C28, C29, C30, C31, C32, C33, C34, C35, C36, C37, C38, C39, C40, C41, C42, C43, C44, C45, C46, C47, C48, C49, C50, C51, C52, C53, C54, C55, C56, C57, C58, C59, C60, C61, C62, C63, C64, C65, C66, C67, C68, C69, C70, C71, C72 | 72 | Yageo | CC0402KRX7R8BB472
DNP | J1 | 0
DNP | J2 | 0
DNP | J3 | 0
RES SMD 100 OHM 0.1% 1/16W 0402 | R1, R2, R3, R4, R5, R6, R7, R8, R9, R10, R11, R12, R13, R14, R15, R16, R17, R18, R19, R20, R21, R22, R23, R24, R25, R26, R27, R28, R29, R30, R31, R32, R33, R34, R35, R36, R37, R38, R39, R40, R41, R42, R43, R44, R45, R46, R47, R48, R49, R50, R51, R52, R53, R54, R55, R56, R57, R58, R59, R60, R61, R62, R63, R64, R65, R66, R67, R68, R69, R70, R71, R72 | 72 | TE Connectivity | CPF0402B100RE1
DNP | R73, R74, R75 | 0

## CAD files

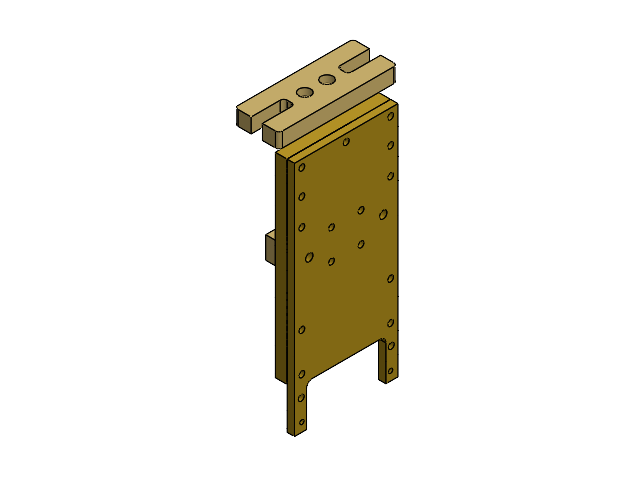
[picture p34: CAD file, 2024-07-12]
cold-assembly/vertical-assembly.SLDASM
HBracket-M4
cold-box-standoff
cold-sample-box-top
cold-sample-box-bottom
cold-box-standoff-T

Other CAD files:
4k-board-standoff/4k-bias-board.step.SLDASM
4k-board-standoff/R1.step.SLDASM
4k-board-standoff/R6.step.SLDASM
4k-board-standoff/R20.step.SLDASM
4k-board-standoff/R10.step.SLDASM
4k-board-standoff/R18.step.SLDASM
4k-board-standoff/Board.step.SLDASM
4k-board-standoff/R7.step.SLDASM
4k-board-standoff/R9.step.SLDASM
4k-board-standoff/R3.step.SLDASM
4k-board-standoff/R2.step.SLDASM
4k-board-standoff/R5.step.SLDASM
4k-board-standoff/R11.step.SLDASM
4k-board-standoff/R4.step.SLDASM
4k-board-standoff/R17.step.SLDASM
4k-board-standoff/R23.step.SLDASM
4k-board-standoff/R13.step.SLDASM
4k-bias-board/4k-bias-board.SLDASM
4k-bias-board/4k-bias-board.SLDDRW
4k-bias-board/4k-bias-board.step
4k-board-standoff/1-0.step.SLDPRT
4k-board-standoff/1.step.SLDPRT
4k-board-standoff/2-1.step.SLDPRT
4k-board-standoff/2.step.SLDPRT
4k-board-standoff/3-2.step.SLDPRT
4k-board-standoff/3.step.SLDPRT
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

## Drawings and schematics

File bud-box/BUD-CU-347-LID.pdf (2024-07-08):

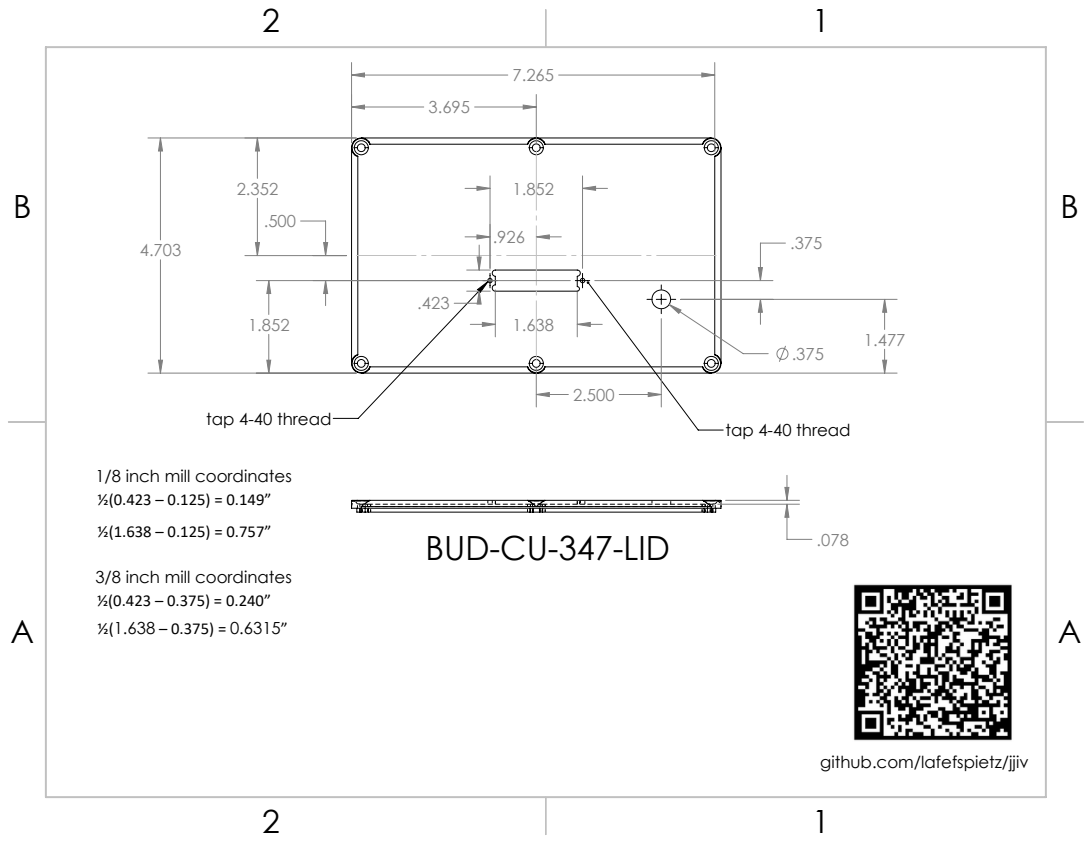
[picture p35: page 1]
tap 4-40 thread; 1/8 inch mill coordinates

BUD-CU-347-LID

3/8 inch mill coordinates

github.com/lafefspietz/jjiv

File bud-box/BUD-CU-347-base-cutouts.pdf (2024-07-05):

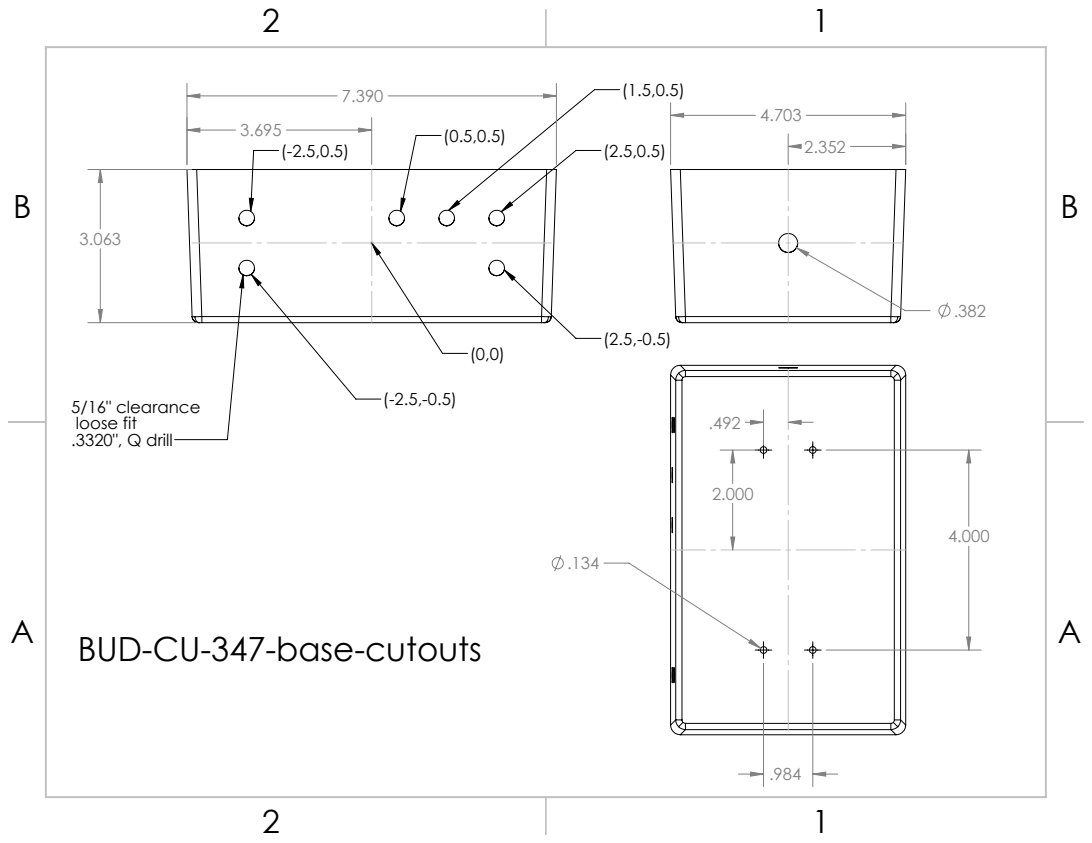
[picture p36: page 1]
5/16" clearance loose fit .3320", Q drill

BUD-CU-347-base-cutouts

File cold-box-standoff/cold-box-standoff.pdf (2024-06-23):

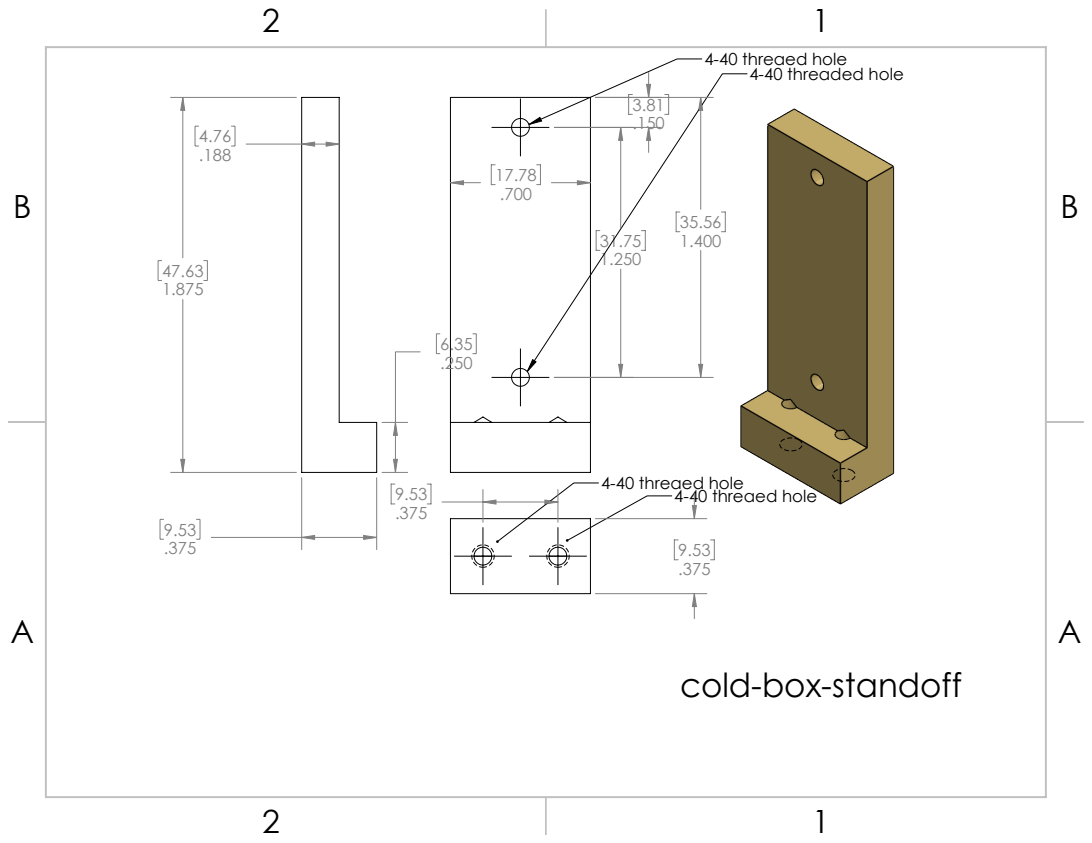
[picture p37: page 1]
4-40 threaed hole 4-40 threaded hole; 4-40 threaed hole

cold-box-standoff

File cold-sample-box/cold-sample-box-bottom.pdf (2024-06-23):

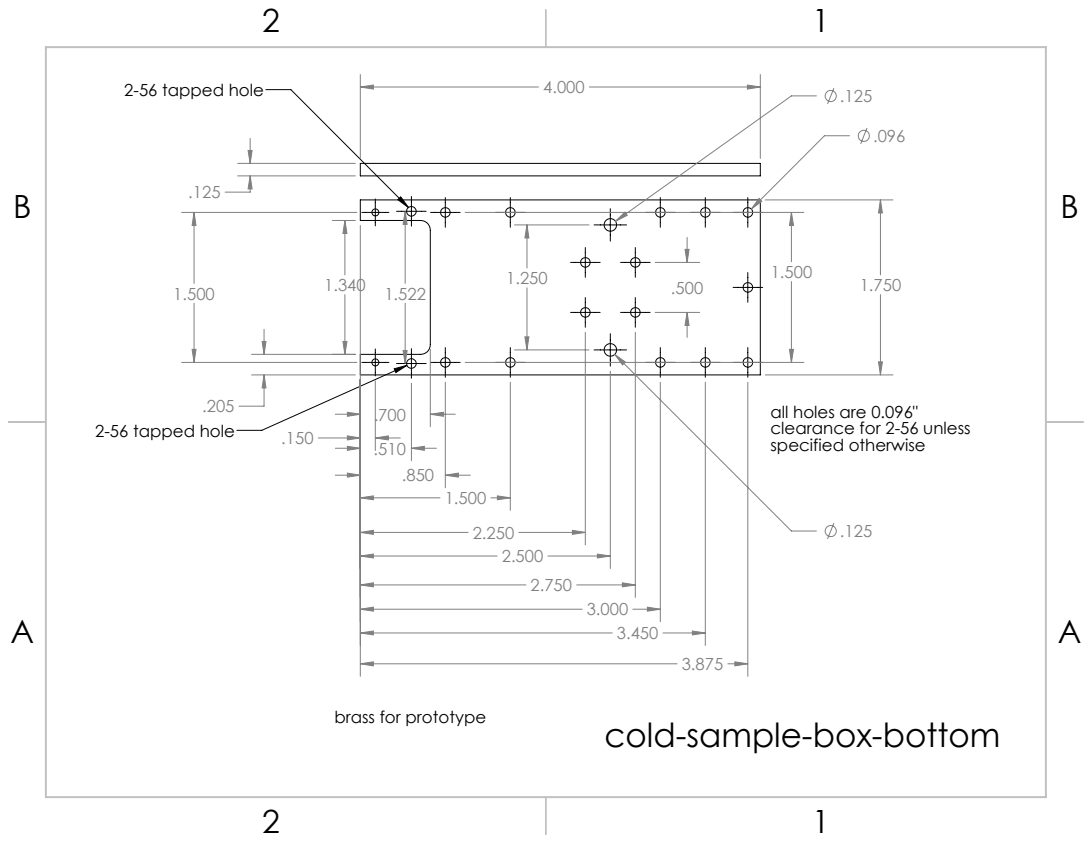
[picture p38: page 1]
2-56 tapped hole

all holes are 0.096"
clearance for 2-56 unless
specified otherwise

brass for prototype

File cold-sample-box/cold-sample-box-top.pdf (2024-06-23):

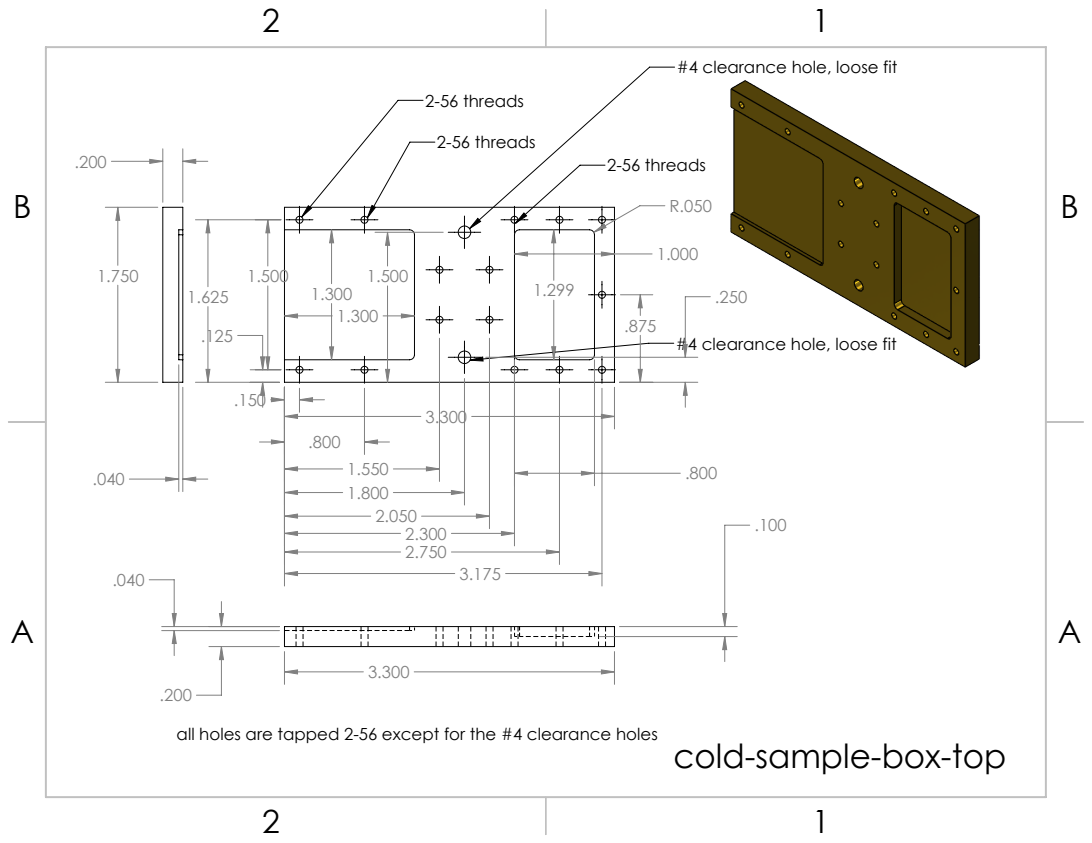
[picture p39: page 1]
2-56 threads

#4 clearance hole, loose fit

all holes are tapped 2-56 except for the #4 clearance holes

cold-sample-box-top

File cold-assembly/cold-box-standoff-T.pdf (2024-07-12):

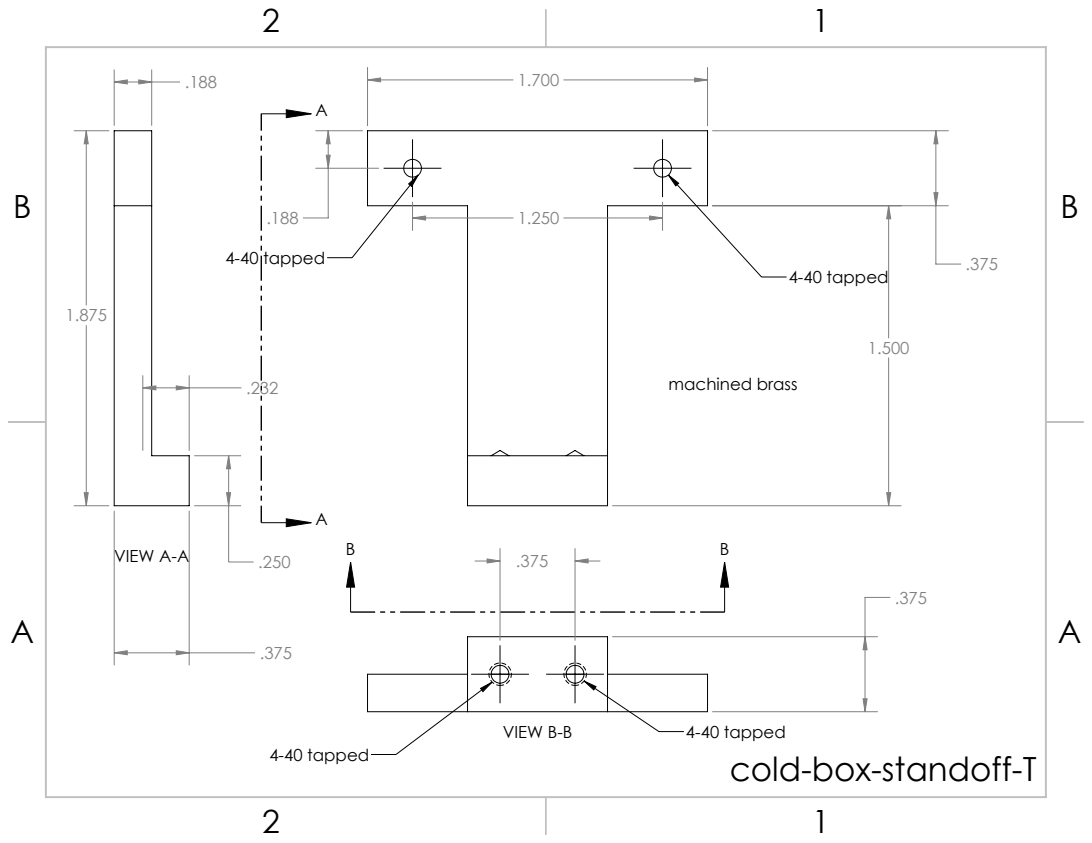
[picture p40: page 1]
4-40 tapped; machined brass; VIEW A-A; VIEW B-B

cold-box-standoff-T

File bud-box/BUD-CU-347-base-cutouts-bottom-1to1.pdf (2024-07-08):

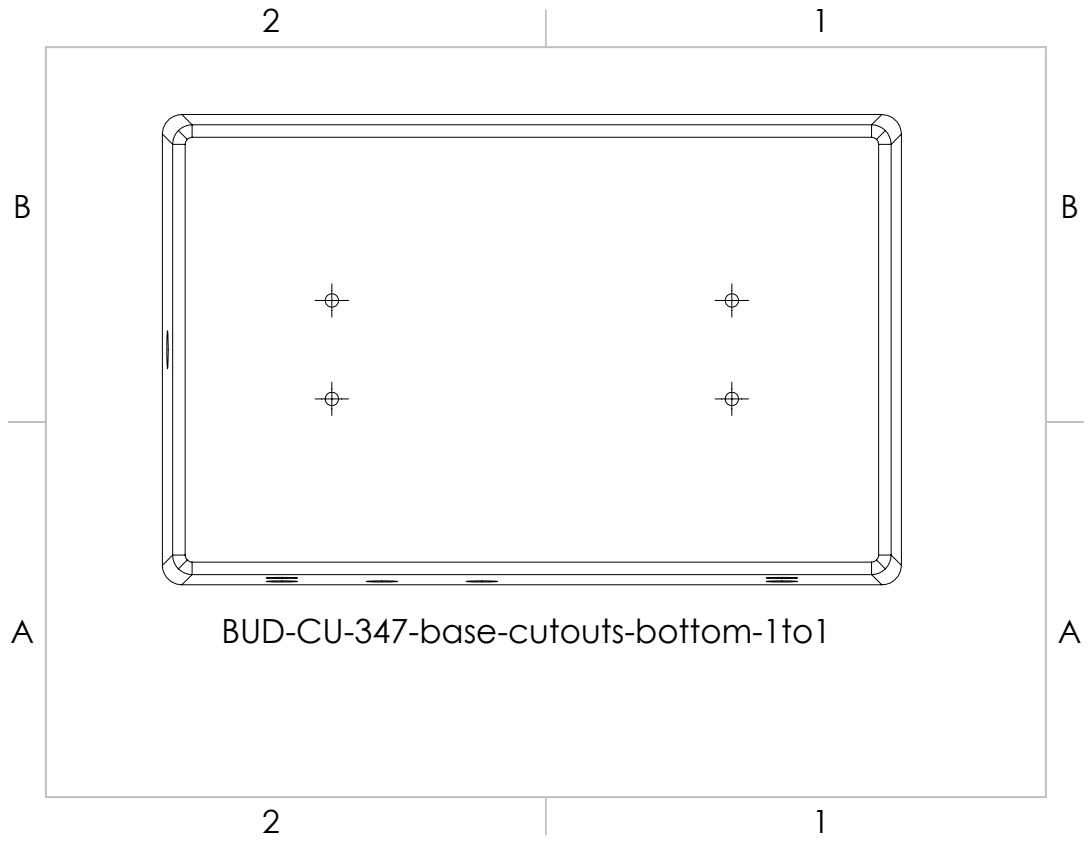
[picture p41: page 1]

BUD-CU-347-base-cutouts-bottom-1to1

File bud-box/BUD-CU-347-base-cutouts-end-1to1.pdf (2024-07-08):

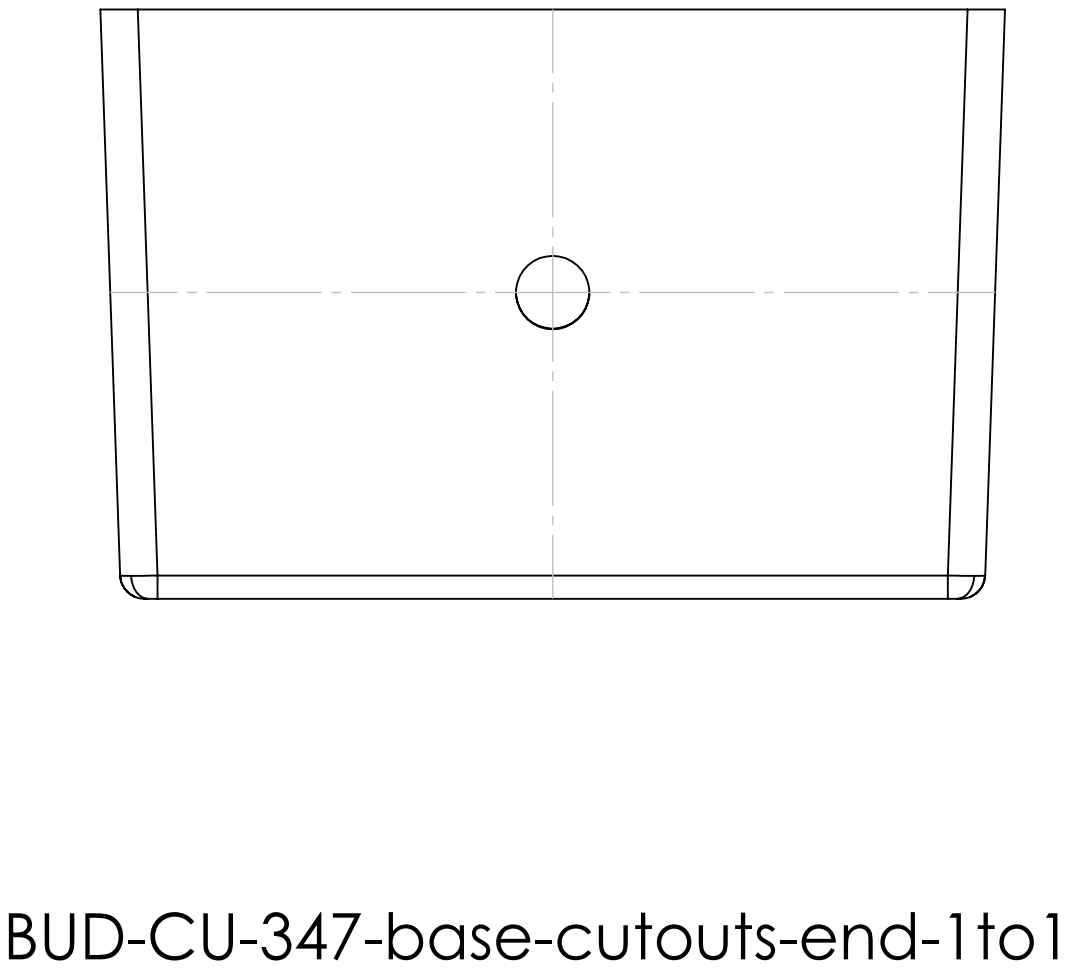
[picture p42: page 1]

BUD-CU-347-base-cutouts-end-1to1

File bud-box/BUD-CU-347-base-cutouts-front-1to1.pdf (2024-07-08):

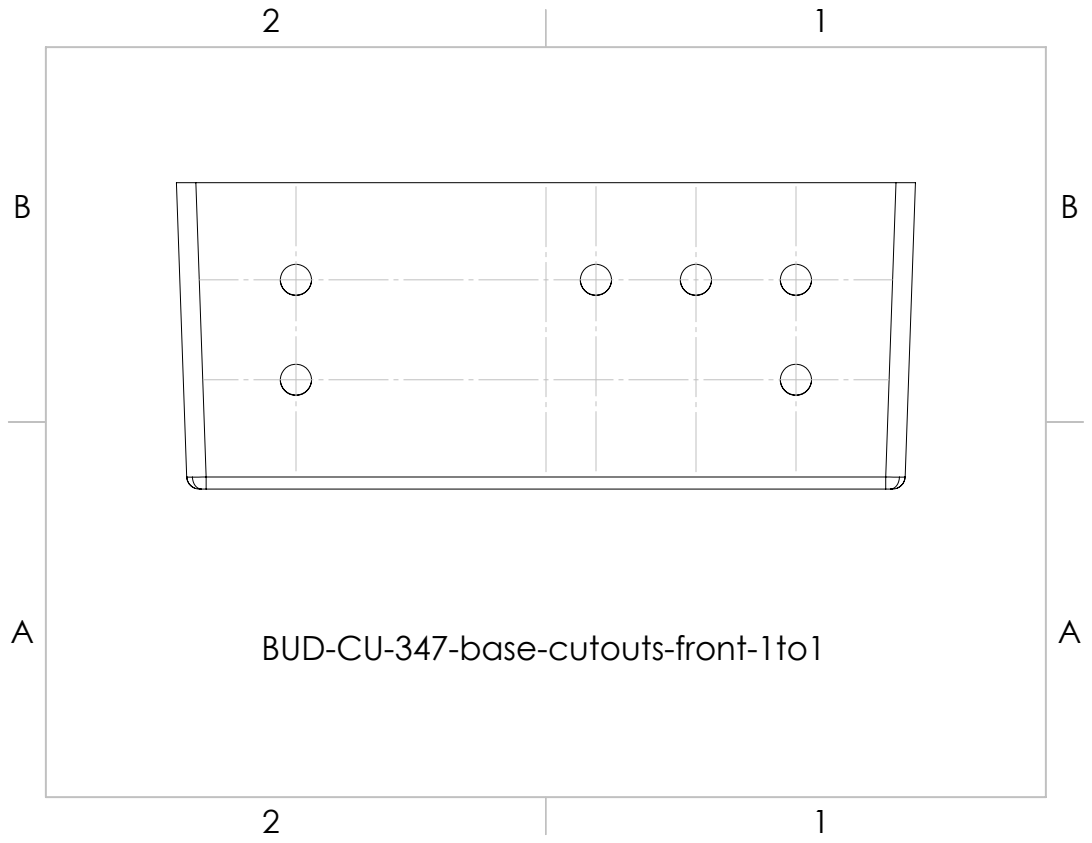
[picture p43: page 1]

BUD-CU-347-base-cutouts-front-1to1

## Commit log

2024-06-23 building out all the elements of the set
    [93465A106_Brass Socket Head Screw.SLDPRT, HBracket-M4.SLDDRW, HBracket-M4.SLDPRT, HBracket-M4.STEP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]
2024-06-23 H Bracket is mostly documented
2024-06-23 H Bracket Readme update
2024-06-23 4d board standoff docs
    [4k-board-standoff.SLDDRW, 4k-board-standoff.SLDPRT]
2024-06-23 4k standoff mostly documented
    [4k-board-standoff.STEP, 4k-board-standoff.STL, 93465A106_Brass-Socket-Head-Screw.SLDPRT]
2024-06-23 4k bias board docs
    [108-0907-001.sldprt, 4k-bias-board-bom.xlsx, 4k-bias-board.PcbDoc, 4k-bias-board.PrjPcb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]
2024-06-23 more docs for 4d bias board
    [1-0.step.SLDPRT, 1.step.SLDPRT, 2-1.step.SLDPRT, 2.step.SLDPRT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]
2024-06-23 way more documentation on 4k board and also cold board
    [1-0.step.SLDPRT, 1.step.SLDPRT, 2-1.step.SLDPRT, 2.step.SLDPRT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]
2024-06-23 cold sample box docs
    [cold-box-standoff.SLDDRW, cold-box-standoff.SLDPRT, cold-box-standoff.STEP, cold-box-standoff.STL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]
2024-06-23 more cold box docs
    [cold-sample-board-rev2-bom.xlsx, cold-sample-board-rev2.PcbDoc, cold-sample-board-rev2.PrjPcb, cold-sample-board-rev2.SchDoc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]
2024-06-24 4k board docs work
2024-07-01 h bracket fully replicating
2024-07-03 cold sample box is really coming together
2024-07-03 readme work on 4k board standoff
2024-07-05 bud box documentation
    [AN-1304-A-lid-machined.SLDDRW, AN-1304-A-machined-box.SLDPRT, AN-1304-A-machined-box.STEP, BUD-CU-347-base-cutouts.SLDDRW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]
2024-07-08 qr code set replicator
    [AN-1304-A-lid-machined.SLDDRW, AN-1304-A-machined-box.SLDPRT, AN-1304-A-machined-box.STEP, BUD-CU-347-LID.SLDDRW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]
2024-07-08 more bud box drawings
    [BUD-CU-347-LID.SLDDRW, BUD-CU-347-LID.SLDPRT, BUD-CU-347-base-cutouts-bottom-1to1.SLDDRW, BUD-CU-347-base-cutouts-end-1to1.SLDDRW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]
2024-07-12 building an assembly of cold parts in order to add another bracket
    [HBracket-M4.SLDPRT, cold-box-standoff.SLDPRT, cold-sample-box-bottom.SLDPRT, cold-sample-box-top.SLDPRT]
2024-07-12 added a T shaped standoff bracket for vertical mounting of cold enclosure
    [cold-box-standoff-T.SLDDRW, cold-box-standoff-T.SLDPRT, cold-box-standoff-T.STEP, vertical-assembly.SLDASM]
